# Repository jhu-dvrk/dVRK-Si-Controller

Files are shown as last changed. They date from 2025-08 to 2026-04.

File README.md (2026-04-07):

# dVRK-Si Controller

This repository contains the documentation to build and test a da Vinci Research Kit Si (dVRK-Si) controller.
For more information about the dVRK, see the [documentation](https://dvrk.readthedocs.io).

## Source Files (in repository)

* `dVRK-Si-Controller-BOM.xlsx`: Bill of Materials
* `dVRK-Si-Controller-Assembly.pptx`: Assembly instructions
* `dVRK-Si-Controller-Testing.docx`: Test instructions
* `dVRK-Si-Controller-Chassis-Graphics.svg`: Design of graphics (labels) for enclosure
* `12v_wire_guide.step`: Design file for custom wire guide used inside controller

## Release Files (Assets in [Releases](https://github.com/jhu-dvrk/dVRK-Si-Controller/releases/latest))

* `dVRK-Si-Controller-BOM.pdf`: Bill of Materials (PDF)
* `dVRK-Si-Controller-Assembly.pdf`: Assembly instructions (PDF)
* `dVRK-Si-Controller-Testing.pdf`: Test instructions (PDF)
* `12v_wire_guide.stl`: STL file for custom wire guide
* `dVRK-Si-Controller-Chassis-Rev*.zip`: ZIP file of chassis design (SolidWorks format)
* `dVRK-Si-Controller-Chassis-Rev*-Graphics.pdf`: Chassis graphics (PDF)

## Links to custom electronics and embedded software

* [FPGA V3](https://github.com/jhu-cisst/FPGA1394V3)
* [DRAC](https://github.com/jhu-dvrk/drac)
* [Front Panel LED](https://github.com/jhu-dvrk/dvrk-si-front-panel-led)
* [Aux I/O Board](https://github.com/jhu-cisst/FPGA1394V3-IO-PCB)
* [FPGA V3 embedded software](https://github.com/jhu-cisst/mechatronics-embedded)
* [dVRK-Si Controller Test Board](https://github.com/jhu-dvrk/dvrk-si-test-board)

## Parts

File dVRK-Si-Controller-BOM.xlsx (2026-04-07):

 | dVRK-Si Controller, Rev 1.1.0
 | Bill of Materials
 | 2026-04-03
Ref | Qty | Description | Notes | Manufacturer | Manufacturer P/N | Supplier | Supplier P/N
 |  | Electronics
101 | 1 | dRAC V3.4 |  | JHU | Design Files (https://github.com/jhu-dvrk/drac/releases/latest) | Avcom
102 | 1 | FPGA V3.x (x = 1 or 2) |  | JHU | Design Files (https://github.com/jhu-cisst/FPGA1394V3) | Avcom
103 | 1 | Front panel LED V2.1 |  | JHU | Design Files (https://github.com/jhu-dvrk/dvrk-si-front-panel-led/releases/latest) | JLCPCB/Avcom
104 | 1 | Power supply, 12V, 50W | 1 | Mean Well | LRS-50-12 | Digikey | 1866-3352-ND
105 | 1 | Power supply, 48V, 300W |  | CUI | VOF-300-48 | Mouser | 490-VOF300-48
106 | 1 | Power entry module |  | TE Conn. | PS0S0DHXB | Digikey | PS0S0DHXB-ND
107 | 6 | Light pipe |  | VCC | LCS_032_CTP | Digikey | LCS_032_CTP-ND
108 | 5 | Thermal interface material |  | t-Global | TG-A6200-19.50-12.70-1.0 | Digikey | 1168-TG-A6200-19.50-12.70-1.0-ND
109 | 2 | Fuse, Ceramic, 10A, 250 VAC, Slow Blow, 5x20mm |  | Generic |  | Digikey | 5923-5HT5-R-ND
110 | 1 | MicroSD Card, Industrial, 16 GB |  | SanDisk |  | Amazon | B094L8N76D
111 | 1 | dVRK Aux I/O V1 |  | JHU | Design Files (https://github.com/jhu-cisst/FPGA1394V3-IO-PCB/releases/tag/v1) | JLCPCB
 |  | Custom wiring harnesses (see Connectors below) | 2
201 | 2 | Wire harness assy, earth 1
202 | 1 | Wire harness assy, earth 2
203 | 1 | Wire harness assy, earth 3
204 | 1 | Wire harness assy, AC
205 | 1 | Wire harness assy, 12V
206 | 1 | Wire harness assy, 48V
207 | 1 | Wire harness assy, front panel
208 | 1 | Wire harness assy, Aux I/O
 |  | Connectors (for custom wiring harnesses)
 | 7 | Conn., Ring, Circ, 16-20 AWG, M3 |  | Generic |  | Digikey | 277-11117-ND
 | 3 | Conn., Quick Connect, RCPT 14-16 AWG, 0.187" |  | TE Conn. | 3-520150-2 | Digikey | A27815CT-ND
 | 4 | Conn., Ring, Circ, 16-22 AWG, M3.5 |  | Generic |  | Digikey | A0956-ND
 | 1 | Conn., Receptacle, 3 Pos, 3.96 mm |  | JST | VHR-3M | Digikey | 455-3982-ND
 | 2 | Wire, Precrimped, SVH-41T-P1.1 X2, 12" |  | JST | ASVHSVH16K305 | Digikey | 455-3107-ND
 | 2 | Conn., Receptacle, 2 Pos, IDC, 22 AWG |  | TE Conn. | 3-644540-2 | Digikey | A31120-ND
 | 2 | Conn., Strain Relief Cover, 2 Pos |  | TE Conn. | 643077-2 | Digikey | A19270-ND
 | 4 | Wire, Precrimped, 24 AWG, Black, 12" |  | JST | ASPHSPH24K305 | Digikey | 455-3083-ND
 | 1 | Conn., Receptacle, 6 Pos, 2 mm |  | JST | PHR-6 | Digikey | 455-1162-ND
 | 1 | Conn., Receptacle, 4 Pos, 2 mm |  | JST | PHR-4 | Digikey | 455-1164-ND
 | 1 | Conn., Plug, 6 Pos, 3.81 mm | 3 | Wurth | 691363310006 | Digikey | 732-691363310006-ND
 | 2 | Conn., Ferrule, DIN, 16 AWG, Black |  | Phoenix Contact | 3200043 | Digikey | 277-2190-ND
 | 4 | Conn., Ferrule, DIN, 24 AWG, Yellow |  | Panduit | FSD73-6-D | Digikey | 298-10284-ND
 | 2 | Conn., Receptacle, 3 Pos, IDC, 22 AWG |  | TE Conn. | 3-644540-3 | Digikey | A31121-ND
 | 2 | Conn., Strain Relief Cover, 3 Pos |  | TE Conn. | A19271-ND | Digikey | A19271-ND
 | 2 | Conn., Receptacle, 6 Pos, 2 mm |  | Hirose | DF11-6DS-2C | Digikey | H2021-ND
 | 6 | Wire, Precrimped, 28 AWG, 8", multiple colors | 7 | Hirose | H3BBT-10108-#8 | Digikey | H3BBT-10108-#8
 |  | Fasteners | 4,5,6
301 | 34 | Screw, M3x5 socket head |  | Generic
302 | 2 | Screw, M3x5 hex countersink |  | Generic
303 | 1 | Screw, M3x20 hex countersink |  | Generic
304 | 3 | Screw, M4x5 hex countersink |  | Generic
305 | 3 | Nut, M3 locking |  | Generic |  | McMaster | 90923A216
306 | 1 | Washer, M3 countersink locking |  | Generic |  | McMaster | 4340N111
307 | 2 | Screwlock, Female, Short |  | TE Conn. | 5207953-3 | Digikey | 5207953-3-ND
308 | 4 | Standoff, Hex, M3x16 female-female |  | Harwin | R30-1011602 | Digikey | 952-1491-ND
 |  | Custom mechanical parts
401 | 1 | Enclosure (bottom 402, front 403, top 404) |  | Protocase | dVRK Si Controller Chassis Rev 4 | Protocase | dVRK Si Controller Chassis Rev 4
405 | 1 | Wire guide, 3D printed, SLS 3201PA-F |  | JHU | 12V_wire_guide | Custom
Notes:
 | 1 | Original part was CUI VGS-50C-12
 | 2 | See assembly instructions for wire/cable specifications
 | 3 | Lower cost alternative is Amphenol TS06315A0000G (Digikey P/N 609-3790-ND)
 | 4 | All fasteners are 18-8 stainless steel unless otherwise specified.
 | 5 | All screws, including 307, must be installed with purple threadlocker or have a pre-applied nylon patch.
 | 6 | Top panel screws provided by Protocase
 | 7 | Replace # by wire color (B=black, W=white, G=green, R=red, L=blue, A=amber)

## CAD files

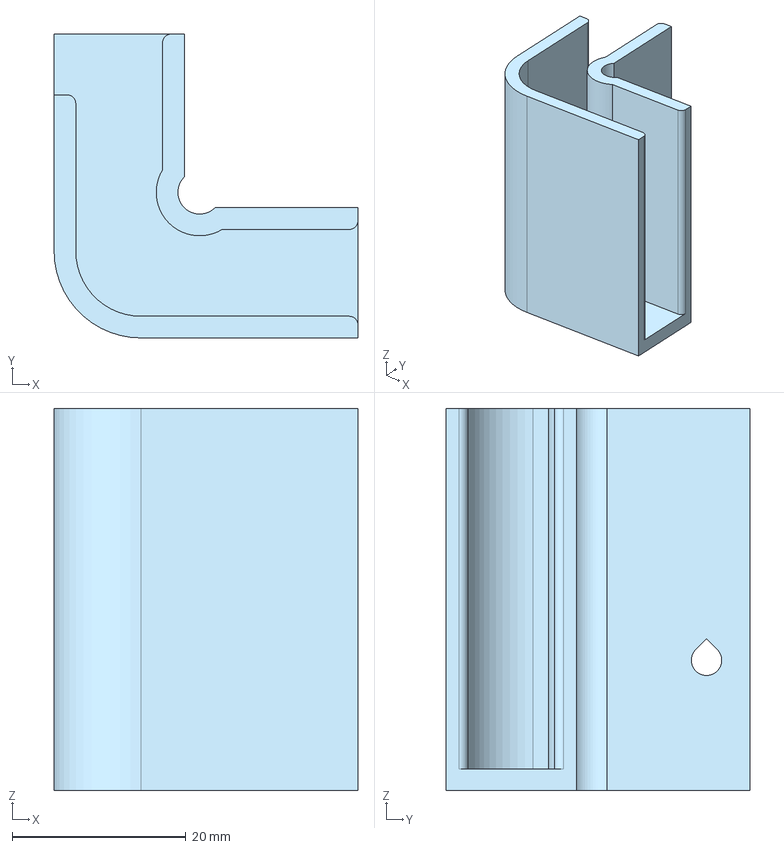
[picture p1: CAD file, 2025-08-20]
12v_wire_guide.step
35.0 x 35.0 x 44.0 mm

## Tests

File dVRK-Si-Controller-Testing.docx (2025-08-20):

# dVRK Si controller testing instructions

v1 2/2024

This documentation explains how to test dVRK Si controllers after assembly.

# Hardware setup

The order of plugging in things does not matter. Just make sure you apply power last.

1. Insert an SD card with the latest firmware in SD card slot on the front panel.
2. Plug in the firewire cable to computer on front panel.
3. Plug in the safety chain test plug (1) on back panel.
4. Plug in the dVRK Si Controller Test board (2) on back panel.
5. Plug in the power cable and turn on the power switch. The front panel LED will display a chaser pattern for about 30 seconds, then after booting complete, change to green PL light and yellow ESPM light.

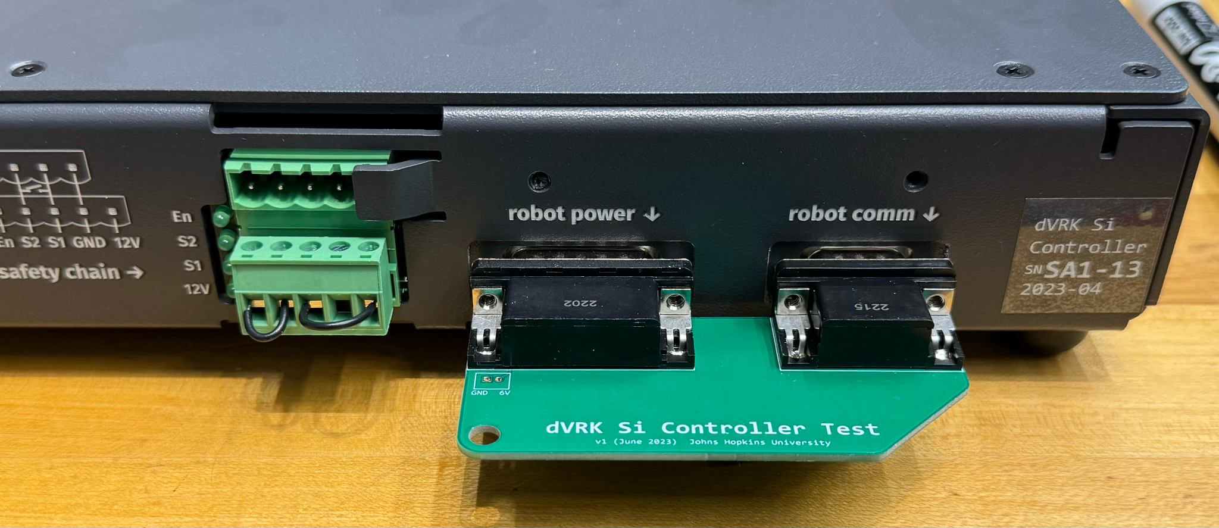
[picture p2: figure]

1

2

# Test program setup

1. Setup the linux test computer with the following script using “all” option:

https://github.com/jhu-dvrk/dvrk-mfg-test/

In step 6, run “sh scripts/setup.sh all”

You should get a dRAC Test icon on desktop.

# Test program run

1. Run dRAC Test on desktop.

2. Choose board ID to match the FPGA board (4, 6, 8, or 10). Choose the protocol (firewire), and click “Connect”

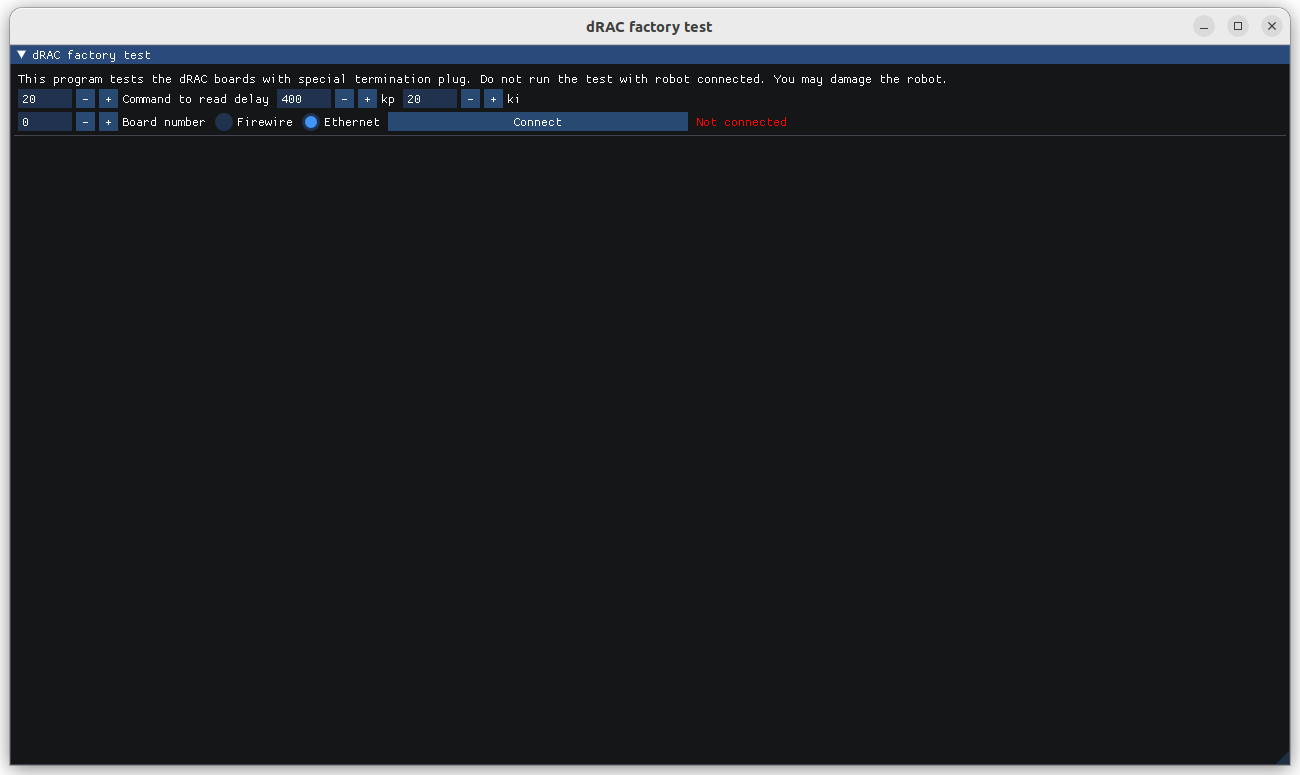
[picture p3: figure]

Sometimes the board takes a while to show up. Retry by clicking “connect” again.

3. Upon successful connect, you will see this.

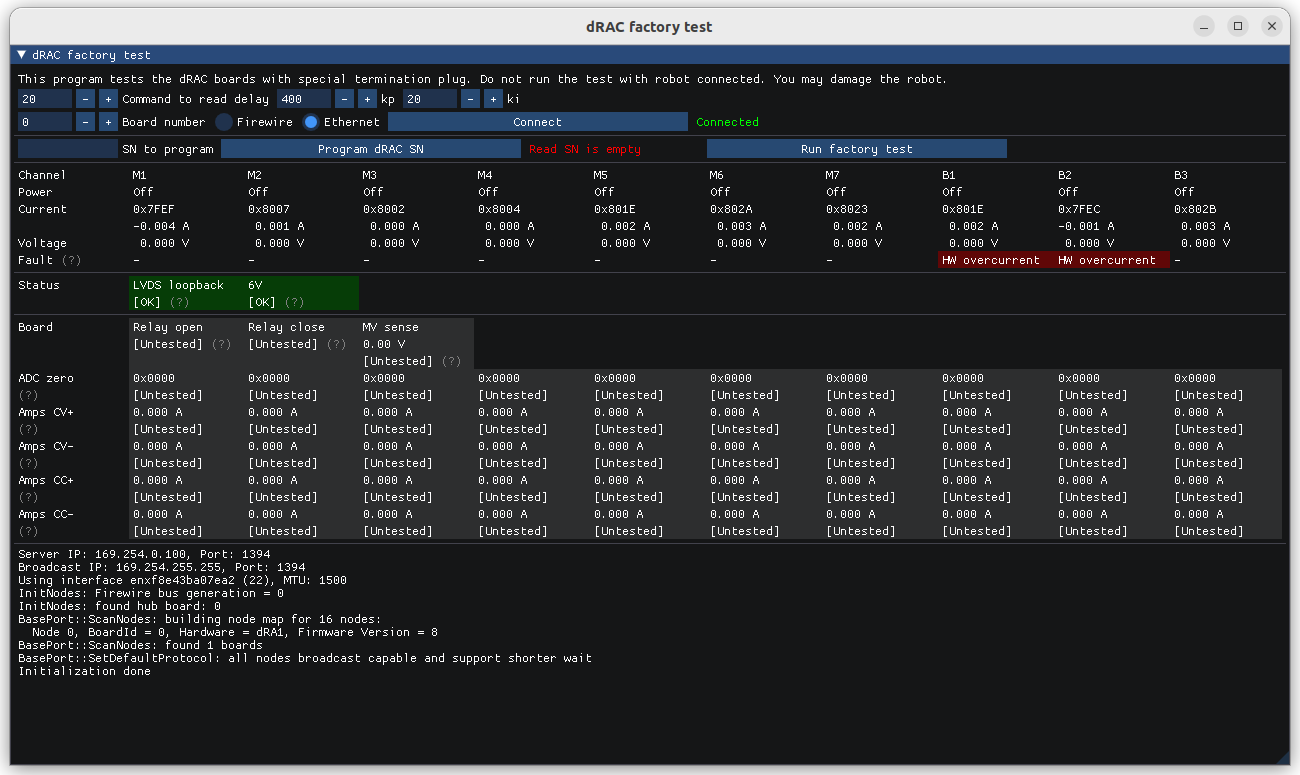
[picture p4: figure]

4. Run the tests. Click .

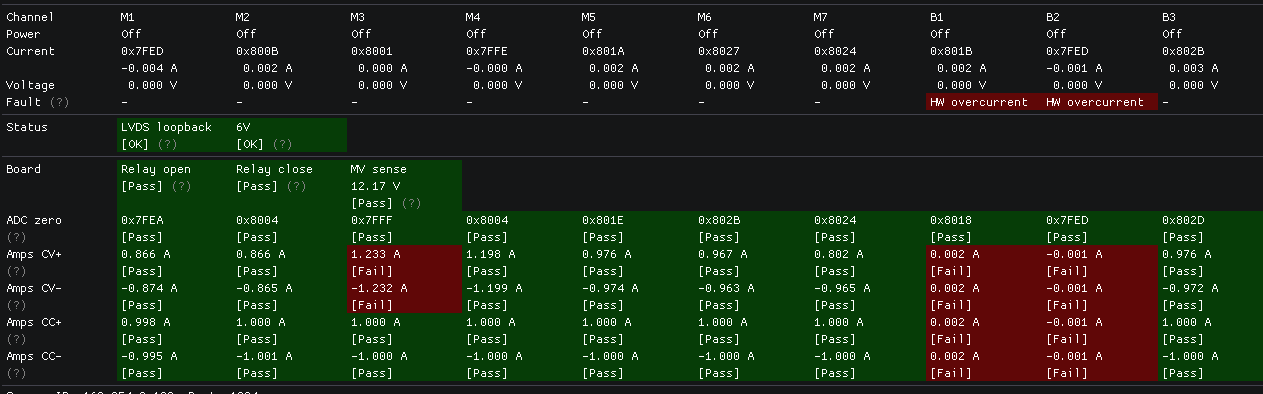
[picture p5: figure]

The test takes a couple seconds to complete. The red-marked items failed the test.

When a channel has a fault, it cannot turn on, and it will cause the tests in that channel to fail. Resolve the fault first. You can retry by clicking the run test button again.

All boxes should be green for the controller to be considered test pass.

The result files are saved in a folder named “dRAC_test_results”. Every time you click the test button, it creates a new file. The file name is “dRAC_[date-time]_[SN].txt”

5. Keep the window open when you are done with this controller. Simply power off the controller, and the program will automatically disconnect. Communication failure messages are expected. When you are ready for the next controller, click “connect” again.

Johns Hopkins University2

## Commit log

2025-08-20 Changed version to 1.0.1
    [dVRK-Si-Controller-BOM.xlsx]
2025-08-20 Added link to dVRK-Si test board
2025-08-21 BOM cost update
    [dVRK-Si-Controller-BOM.xlsx]
2025-08-21 Removed estimated component costs from BOM
    [dVRK-Si-Controller-BOM.xlsx]
2025-08-21 Fixed BOM formatting
    [dVRK-Si-Controller-BOM.xlsx]
2025-09-03 Updated ReadMe to specify asset files in Releases; updated P/N for chassis in BOM
    [dVRK-Si-Controller-BOM.xlsx]
2026-04-04 Updates for Rev 4
    [dVRK-Si-Controller-BOM.xlsx]
2026-04-06 Minor update to assembly
2026-04-07 Moved V1.1.0 (Rev4 chassis) assembly instructions to end
2026-04-07 Added link to Aux I/O board design
